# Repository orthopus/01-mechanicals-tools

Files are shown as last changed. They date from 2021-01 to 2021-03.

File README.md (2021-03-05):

# Mechanicals Tools for hand amputees




This repository contains documentation of mechanicals tools dedicated to daily life use: suitable tools to practice music, sports, cooking, etc!

For now you will find : 

- **a guitar pick holder 3D printed**
- **a tennis ball holder 3D printed** 

These tools can be used with the [ORTHOPUS' universal mechanical wrist](https://github.com/orthopus/01-wrist).

## WARNING NOTICE BEFORE STARTING

The versions of our solutions reproduced with Do It Yourself technics will not be CE marked. It can only be applied to solutions developed and sold by ORTHOPUS which follow the applicable regulations.
ORTHOPUS cannot guarantee the “quality” of solutions replicated by third parties thanks to documentation shared on github.

## GUITAR PICK HOLDER 3D PRINTED

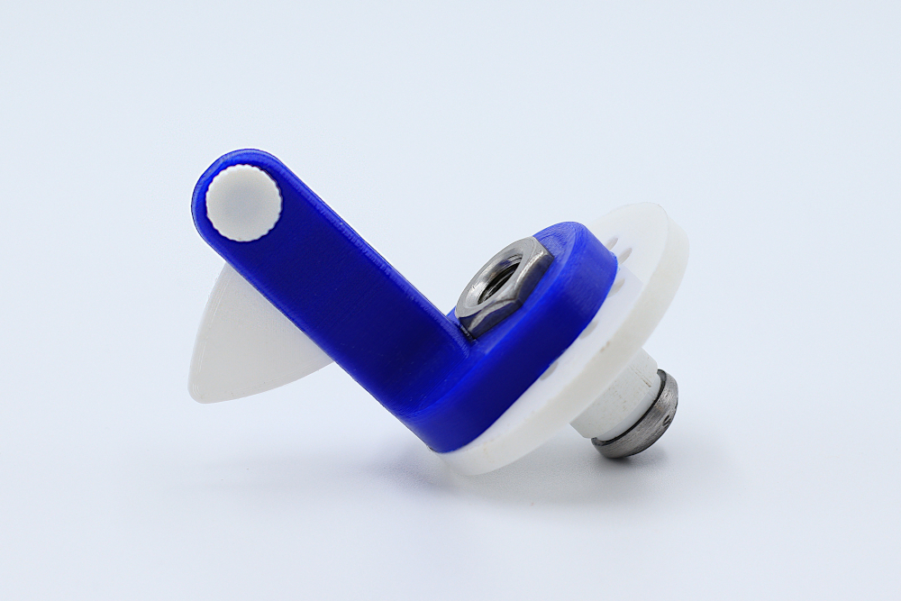
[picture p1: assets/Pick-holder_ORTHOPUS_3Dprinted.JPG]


### D.I.Y Level **⭐**

**Required components**: To make your own Pick Holder, you will need a 3D printer, a guitar pick, a Tool Holder 3D printed ([Making Manual](https://github.com/orthopus/01-wrist/blob/main/docs/tool-holder-3D-printer/ToolHolder_3D_making-manual.md)) and some basics screws (you will find a detailed list of equipment in the [Making Manual](https://github.com/orthopus/01-mechanicals-tools/blob/main/docs/PickHolder_making-manual.md))

**How to make your own**: you can make the Pick Holder for ~2€: more details in the Bill of Material shown below and available with clickable links [here](https://github.com/orthopus/01-mechanicals-tools/blob/main/src/GuitarPickHolder-3D/ILL-0307-%20Pick%20Holder%203D%20printed_BoM.pdf).

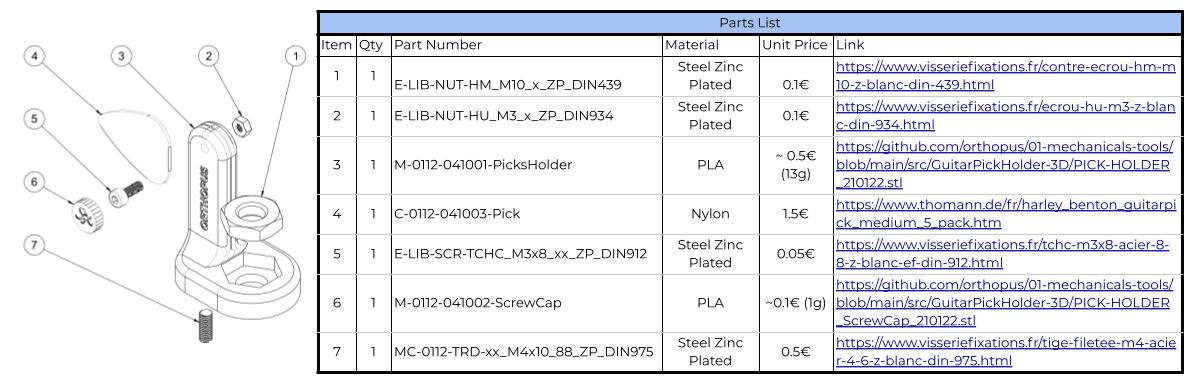
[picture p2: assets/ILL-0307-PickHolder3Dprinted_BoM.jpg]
ILL-0307-PickHolder3Dprinted_BoM


To make your own Pick Holder, follow the [Making Manual](https://github.com/orthopus/01-mechanicals-tools/blob/main/docs/PickHolder_making-manual.md).

## TENNIS BALL HOLDER 3D PRINTED

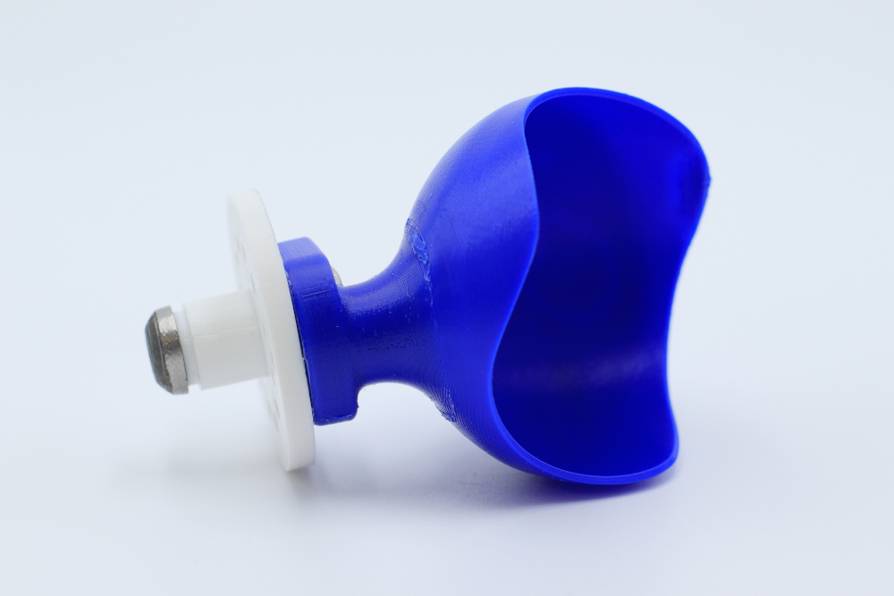
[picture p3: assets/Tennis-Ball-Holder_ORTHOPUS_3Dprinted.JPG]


### D.I.Y Level **⭐**

**Required components**: To make your own Tennis Ball Holder, you will need a 3D printer, a metal saw, a Tool Holder 3D printed ([Making Manual](https://github.com/orthopus/01-wrist/blob/main/docs/tool-holder-3D-printer/ToolHolder_3D_making-manual.md)) and some basics screws (you will find a detailed list of equipment in the [Making Manual](https://github.com/orthopus/01-mechanicals-tools/blob/main/docs/TennisBallHolder_making-manual.md)).

**How to make your own**:

You can make the Tennis Ball Holder for ~2.5€: more details in the Bill of Material shown below and available with clickable links [here](https://github.com/orthopus/01-mechanicals-tools/blob/main/src/TennisBallHolder-3D/ILL-0307-TennisBallHolder3Dprinted_BoM.pdf).

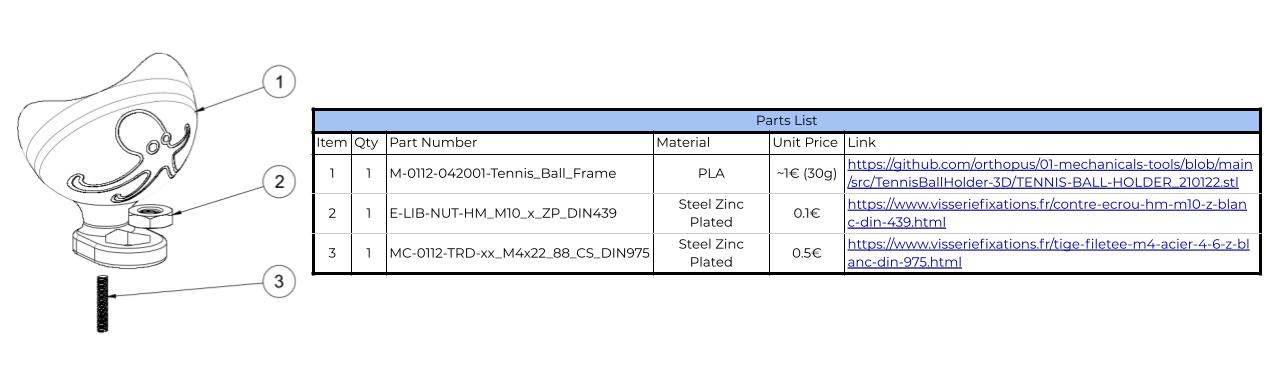
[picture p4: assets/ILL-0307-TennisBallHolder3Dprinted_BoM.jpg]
ILL-0307-TennisBallHolder3Dprinted_BoM


To make your own Tennis Ball Holder, follow the [Making Manual](https://github.com/orthopus/01-mechanicals-tools/blob/main/docs/TennisBallHolder_making-manual.md).

## CONTRIBUTION

Your contribution to the **Tennis Ball Holder v2.0** and the **Pick Holder v2.0** is welcome!

* Have you discovered a bug or you have an improvement ideas ?
  * Go to the GitHub [issues](https://github.com/orthopus/01-mechanicals-tools/issues) of the project.
* You have time, some Maker skills and you want to help us ?
  * ***If you need to make some modifications, our Fusion 360 source files are available on request, don’t hesitate to ask us!***
  * Read the [CONTRIBUTING](CONTRIBUTING‧md) file to help us to upgrade this project
  * Read the [CODEOFCONDUCT](CODEOFCONDUCT‧md) file to know community standards

## CONTACT

If you wish to contact us, you can send a message to contact@orthopus.com

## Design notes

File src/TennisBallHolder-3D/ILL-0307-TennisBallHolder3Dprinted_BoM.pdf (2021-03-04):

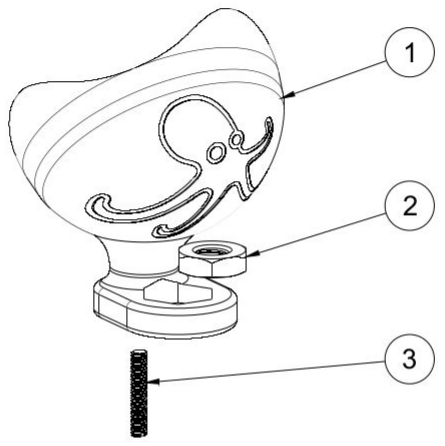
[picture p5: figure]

Parts List (please download this file for clickable links)
Item | Qty | Part Number | Material | Unit Price | Link
1 | 1 | M-0112-042001-Tennis_Ball_Frame | PLA | ~1€ (30g) | https://github.com/orthopus/01-mechanicals-tools/blob/main
/src/TennisBallHolder-3D/TENNIS-BALL-HOLDER_210122.stl (https://github.com/orthopus/01-mechanicals-tools/blob/main/src/TennisBallHolder-3D/TENNIS-BALL-HOLDER_210122.stl)
2 | 1 | E-LIB-NUT-HM_M10_x_ZP_DIN439 | Steel Zinc Plated | 0.1€ | https://www.visseriefixations.fr/contre-ecrou-hm-m10-z-blan
3 | 1 | MC-0112-TRD-xx_M4x22_88_CS_DIN975 | Steel Zinc Plated | 0.5€ | https://www.visseriefixations.fr/tige-filetee-m4-acier-4-6-z-bl

c-din-439.html (https://www.visseriefixations.fr/contre-ecrou-hm-m10-z-blanc-din-439.html)

anc-din-975.html (https://github.com/orthopus/01-mechanicals-tools/blob/main/src/GuitarPickHolder-3D/PICK-HOLDER_210122.stl)

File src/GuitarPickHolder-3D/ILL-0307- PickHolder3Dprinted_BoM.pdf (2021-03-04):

Parts List (please download this file for clickable links)
Item | Qty | Part Number | Material | Unit Price | Link
1 | 1 | E-LIB-NUT-HM_M10_x_ZP_DIN439 | Steel Zinc Plated | 0.1€ | https://www.visseriefixations.fr/contre-ecrou-hm-m

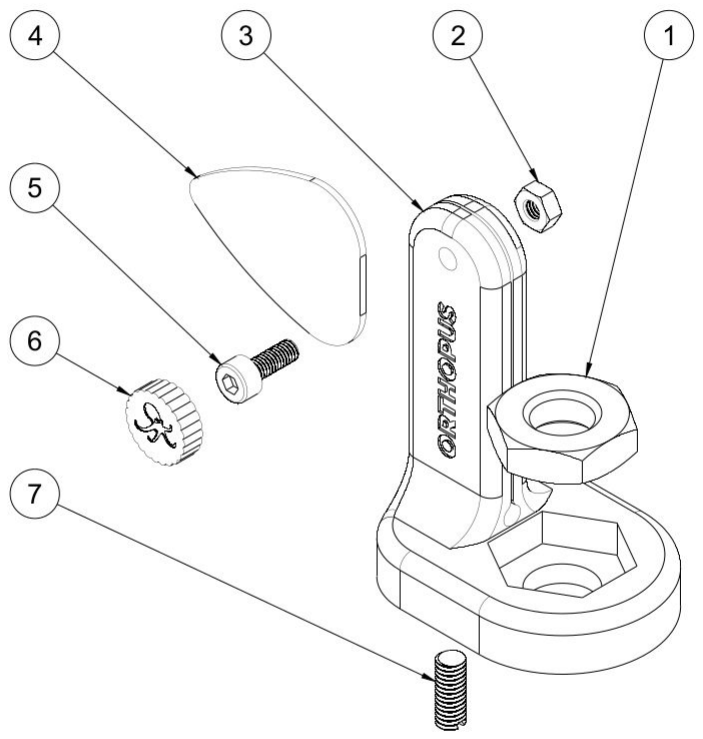
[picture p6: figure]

2 | 1 | E-LIB-NUT-HU_M3_x_ZP_DIN934 | Steel Zinc Plated | 0.1€ | https://www.visseriefixations.fr/ecrou-hu-m3-z-blan
3 | 1 | M-0112-041001-PicksHolder | PLA | ~ 0.5€ (13g) | https://github.com/orthopus/01-mechanicals-tools/blob/main/src/GuitarPickHolder-3D/PICK-HOLDER
4 | 1 | C-0112-041003-Pick | Nylon | 1.5€ | https://www.thomann.de/fr/harley_benton_guitarpi
5 | 1 | E-LIB-SCR-TCHC_M3x8_xx_ZP_DIN912 | Steel Zinc Plated | 0.05€ | https://www.visseriefixations.fr/tchc-m3x8-acier-8-

10-z-blanc-din-439.html (https://www.visseriefixations.fr/contre-ecrou-hm-m10-z-blanc-din-439.html)

c-din-934.html (https://www.visseriefixations.fr/ecrou-hu-m3-z-blanc-din-934.html)

_210122.stl (https://github.com/orthopus/01-mechanicals-tools/blob/main/src/GuitarPickHolder-3D/PICK-HOLDER_210122.stl)

ck_medium_5_pack.htm (https://www.thomann.de/fr/harley_benton_guitarpick_medium_5_pack.htm)

8-z-blanc-ef-din-912.html (https://www.visseriefixations.fr/tchc-m3x8-acier-8-8-z-blanc-ef-din-912.html)
6 | 1 | M-0112-041002-ScrewCap | PLA | ~0.1€ (1g) | https://github.com/orthopus/01-mechanicals-tools/blob/main/src/GuitarPickHolder-3D/PICK-HOLDER
7 | 1 | MC-0112-TRD-xx_M4x10_88_ZP_DIN975 | Steel Zinc Plated | 0.5€ | https://www.visseriefixations.fr/tige-filetee-m4-acie

_ScrewCap_210122.stl (https://github.com/orthopus/01-mechanicals-tools/blob/main/src/GuitarPickHolder-3D/PICK-HOLDER_ScrewCap_210122.stl)

r-4-6-z-blanc-din-975.html (https://www.visseriefixations.fr/tige-filetee-m4-acier-4-6-z-blanc-din-975.html)

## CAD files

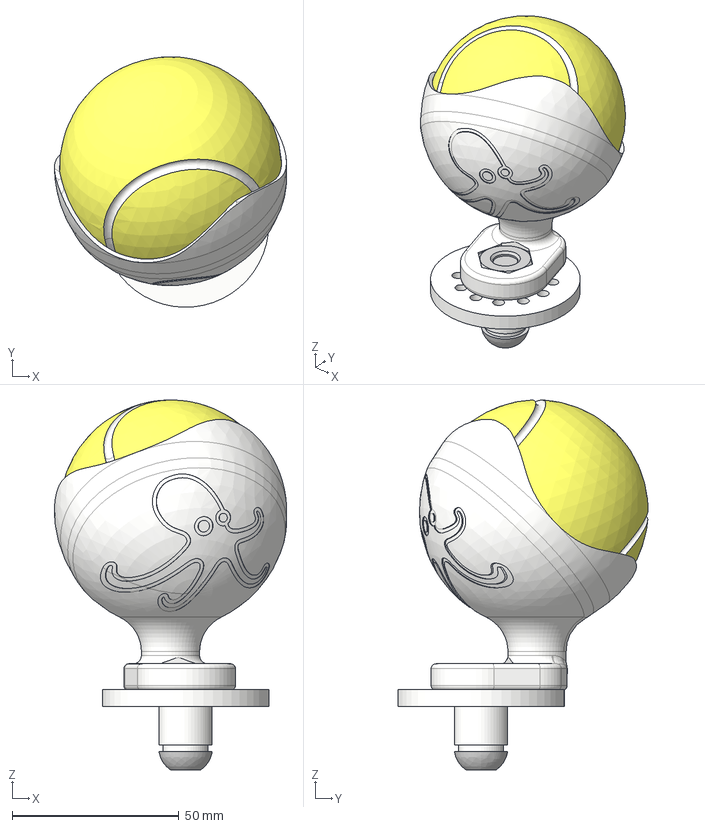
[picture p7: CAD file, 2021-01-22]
src/TennisBallHolder-3D/TENNIS-BALL-HOLDER_210122.step
69.7 x 75.2 x 111.1 mm
M-0109-03_1481-AttachmentPlate_3DP
MC-0109_1482-TBHC_M10X25_00_CS_ISO7380
M-0112-042001-Tennis_Ball_Frame
C-0112-042002-Tennis_Ball
MC-0112-TRD-xx_M4x22_88_CS_DIN975

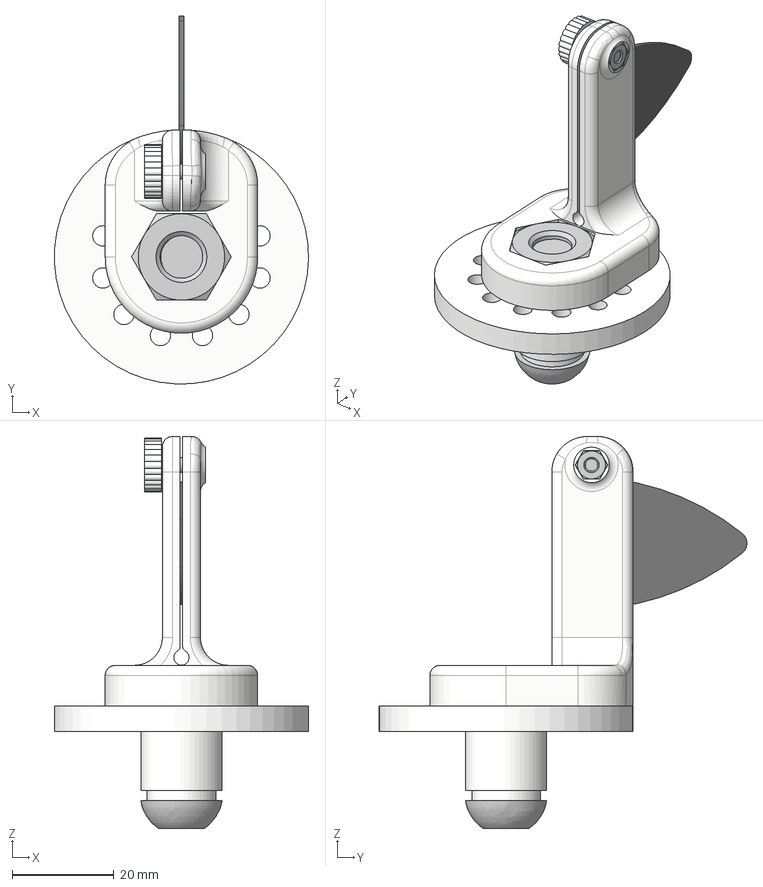
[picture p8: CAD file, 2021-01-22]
src/GuitarPickHolder-3D/PICK-HOLDER_210122.step
50.0 x 72.3 x 77.1 mm
M-0112-041001-PicksHolder
M-0112-041002-ScrewCap
C-0112-041003-Pick
MC-0112-TRD-xx_M4x10_88_CS_DIN975
M-0109-03_1481-AttachmentPlate_3DP
MC-0109_1482-TBHC_M10X25_00_CS_ISO7380

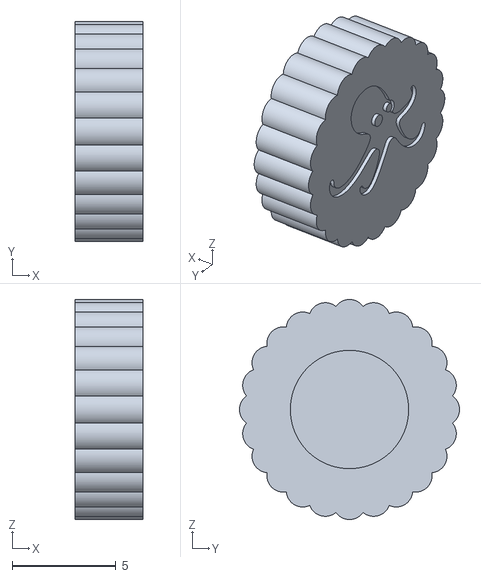
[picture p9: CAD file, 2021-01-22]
src/GuitarPickHolder-3D/PICK-HOLDER_ScrewCap_210122.stl
3.30 x 10.6 x 10.6

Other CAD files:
src/GuitarPickHolder-3D/PICK-HOLDER_210122.stl
src/TennisBallHolder-3D/TENNIS-BALL-HOLDER_210122.stl

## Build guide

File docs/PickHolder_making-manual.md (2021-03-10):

# Pick Holder 3D : Making Manual

In this manual, you will find all the resources to design the ORTHOPUS 3D printed Pick Holder.

Pick-holder_ORTHOPUS_3Dprinted

### **List of Equipment**

**To design the Pick Holder you will need :**

- PLA type filament
- A Tool Holder 3D printed ([Making Manual](https://github.com/orthopus/01-wrist/blob/main/docs/tool-holder-3D-printer/ToolHolder_3D_making-manual.md))
- A threaded rod M4, zinc plated, DIN 975
- A screw (CHC M3x8, zinc plated, DIN 912)
- A bolt (Hu M3, zinc plated, DIN 934)

More details in the Bill of Material shown below and available with clickable links [here](https://github.com/orthopus/01-mechanicals-tools/blob/main/src/GuitarPickHolder-3D/ILL-0307-%20PickHolder3Dprinted_BoM.pdf).

ILL-0307-PickHolder3Dprinted_BoM

**Tools :**

- A 3D Printer

- Cyanoacrylate glue (super glue)

### **The 3D printed body**

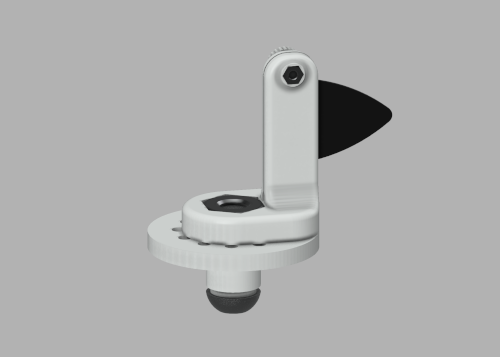
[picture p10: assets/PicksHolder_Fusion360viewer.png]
PicksHolder_Fusion360viewer (https://a360.co/3dsERMs)


🧐 *Tip : open the image in a new tab to view the Pick Holder in Fusion 360 viewer*

The 3D printed body of the **Pick Holder** will firmly hold guitar picks. It will allow you through a tightening system to adjust the position and to adapt to the thickness of the guitar pick. This body needs to be connected to the **[Tool Holder 3D printed](https://github.com/orthopus/01-wrist).**

The 2 .STL file are available in [the SRC repository](https://github.com/orthopus/01-mechanicals-tools/tree/main/src/GuitarPickHolder-3D)

We used the Ultimaker Cura slicer and an Ultimaker Extended 2+ 3D printer. Following parameter were used:

- Layer height: 0.15 mm

- Infill density: 50%

- Print speed: 50 mm/s

- Fan speed: 100%

- Build plate adhesion type: Brim

### **Machining Operation**

To avoid the pick holder to get loose from the tool holder 3D printed, a modified threaded rod needs to be made. With a metal saw, saw a M4 threaded rod or a M4 screw to get a 10 mm threaded part. To be able to screw this threaded part inside the Pick Holder, it is necessary to make a slot at one end of it. Using the saw, make a ~1 mm deep slot to be able to use a flat screwdriver to screw the threaded part inside the Tennis Ball Holder.

You should get the following part:

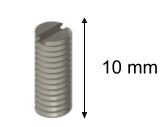
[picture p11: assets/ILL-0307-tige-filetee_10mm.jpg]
ILL-0307-tige-filetee_10mm


### **Assembly**

- **Assembly of the pick holder 3D printed:**

1. First, insert the 10 mm long threaded rod into the 3D printed body with a flat screwdriver. 
2. Glue the head of the screw in the screw cap. 
3. Place the M3 bolt in its housing. Then insert inside the screw with the glued cap.
4. You can now insert a guitar pick in the slot. You need to adjust the position of the screw to let the pick in the slot and then to hold it firmly.

- **Assembly of the pick holder 3D printed onto the Tool Holder 3d printed:**

1. Place the M10 bolt in its housing and the 3D printed body over the Tool Holder 3D Printed (a Tool Holder 3D printed [Making Manual](https://github.com/orthopus/01-wrist/blob/main/docs/tool-holder-3D-printer/ToolHolder_3D_making-manual.md)). Be careful to place the 10 mm long threaded rod into the specific hole of the Tool Holder 3D Printed.

2. Screw the M10 modified screw in the M10 bolt.

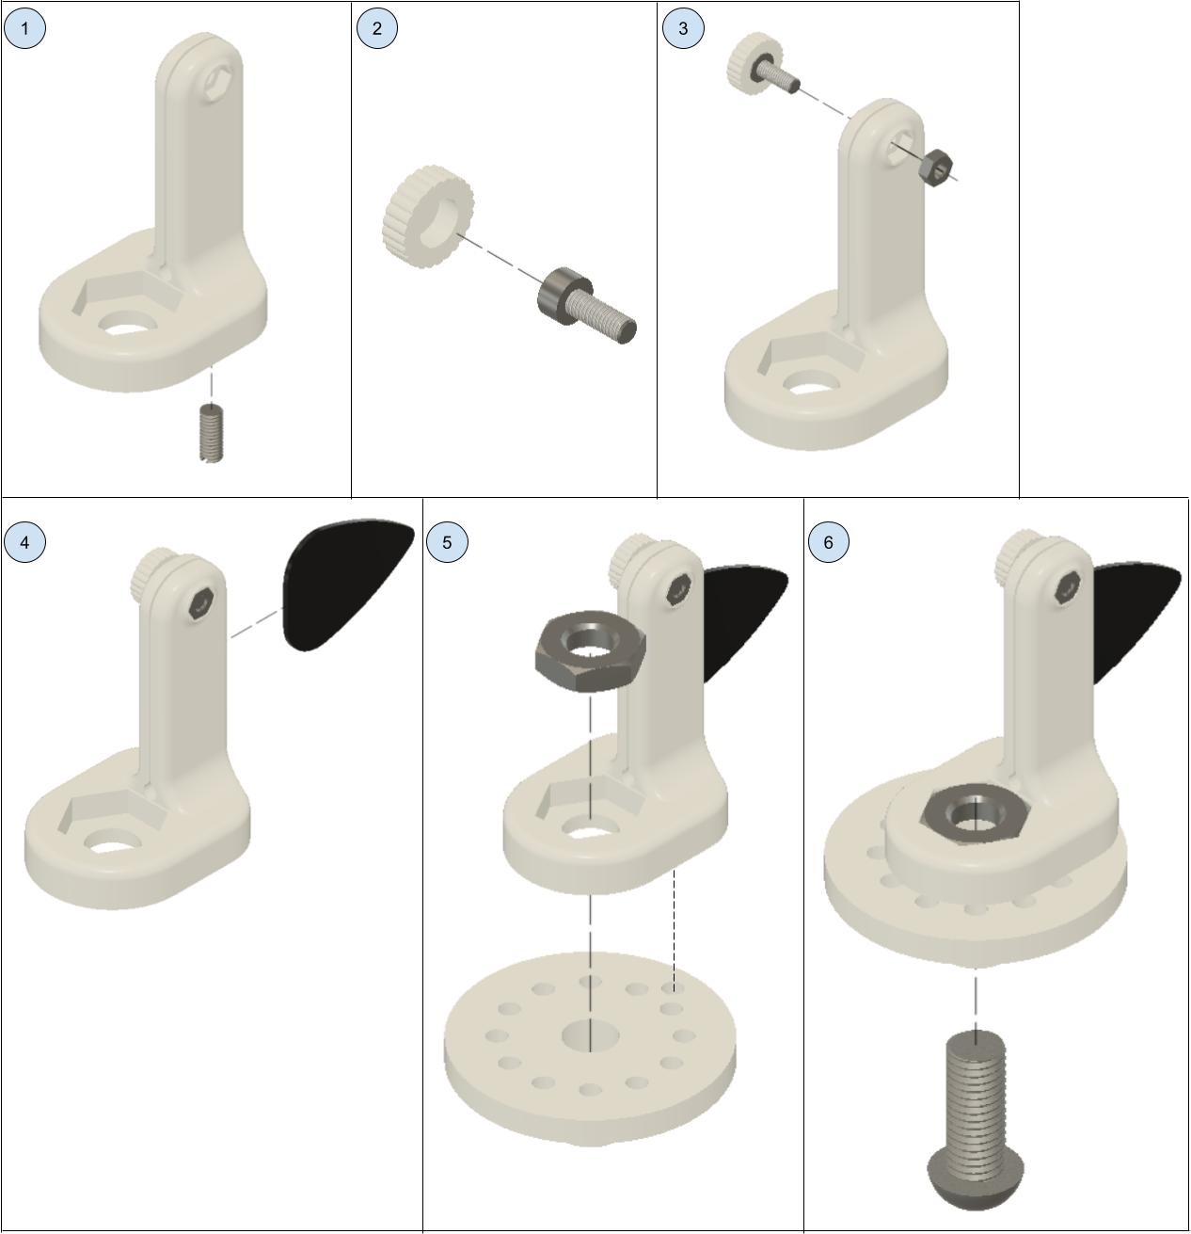
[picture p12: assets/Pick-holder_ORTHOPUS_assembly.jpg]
Pick-holder_ORTHOPUS_assembly


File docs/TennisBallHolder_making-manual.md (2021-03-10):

# Tennis Ball Holder : Making Manual

Tennis-Ball-Holder_ORTHOPUS_3Dprinted

In this manual, you will find all the resources to design the ORTHOPUS' 3D printed Tennis Ball Holder.

### **List of Equipment**

**To design the Tennis Ball Holder you will need :**

- PLA type filament
- A Tool Holder 3D printed [Making Manual](https://github.com/orthopus/01-wrist/blob/main/docs/tool-holder-3D-printer/ToolHolder_3D_making-manual.md)
- A threaded rod M4, zinc plated, DIN 975
- a Tool Holder 3D printed

More details in the Bill of Material shown below and available with clickable links [here](https://github.com/orthopus/01-mechanicals-tools/blob/main/src/TennisBallHolder-3D/ILL-0307-TennisBallHolder3Dprinted_BoM.pdf).

ILL-0307-TennisBallHolder3Dprinted_BoM

**Tools :** 

- A metal saw
- A 3D Printer

### **The 3D printed body** 

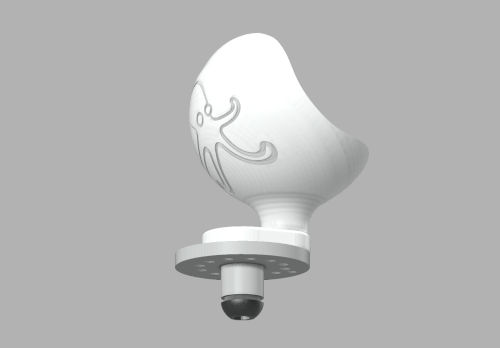
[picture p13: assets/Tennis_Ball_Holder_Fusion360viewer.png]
Tennis_Ball_Holder_Fusion360viewer (https://a360.co/30sFVIv)


🧐 *Tip : open the image in a new tab to view the Tennis Ball Holder in Fusion 360 viewer*

The **Tennis Ball Holder** will house the tennis ball. It will allow you to throw the tennis ball and to serve as a pro! The 3D printed body of the Tennis ball Holder needs to be connected to the **[Tool Holder 3D printed](https://github.com/orthopus/01-wrist).** Thus, to make a Tennis Ball Holder compatible with the Universal Wrist you need to assemble the 3D printed body with a **[Tool Holder 3D printed](https://github.com/orthopus/01-wrist).**

The .STL file are available [here](https://github.com/orthopus/01-mechanicals-tools/tree/main/src/TennisBallHolder-3D)

We used the Ultimaker Cura slicer and an Ultimaker Extended 2+ 3D printer.

**Following parameter were used:**

- Layer height: 0.15 mm
- Infill density: 50%
- Print speed: 50 mm/s
- Fan speed: 100%
- Build plate adhesion type: Brim

### **Machining Operation**

To avoid the tennis ball holder to get loose from the tool holder 3D printed, a modified threaded rod needs to be made. With a metal saw, saw a M4 threaded rod or a M4 screw to get a 22 mm threaded part. To be able to screw this threaded part inside the Tennis Ball Holder, it is necessary to make a slot at one end of it. Using the saw, make a ~1 mm deep slot to be able to use a flat screwdriver to screw the threaded part inside the Tennis Ball Holder.

You should get the following part:

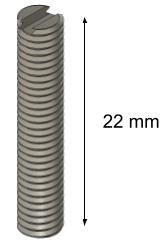
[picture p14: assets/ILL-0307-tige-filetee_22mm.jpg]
ILL-0307-tige-filetee_22mm


### **Assembly**

**Assembly of the Tennis ball holder 3D printed:**

1. First, insert the 22 mm long threaded rod into the 3D printed body with a flat screwdriver.

**Assembly of the Tennis ball holder 3D printed onto the Tool Holder 3D printed**:

1. Place the M10 bolt in its housing and the 3D printed body over the Tool Holder 3D Printed (a Tool Holder 3D printed [Making Manual](https://github.com/orthopus/01-wrist/blob/main/docs/tool-holder-3D-printer/ToolHolder_3D_making-manual.md)). Be careful to place the 22 mm long threaded rod into the specific hole of the Tool Holder 3D Printed.

2. Screw the M10 modified screw in the M10 bolt.

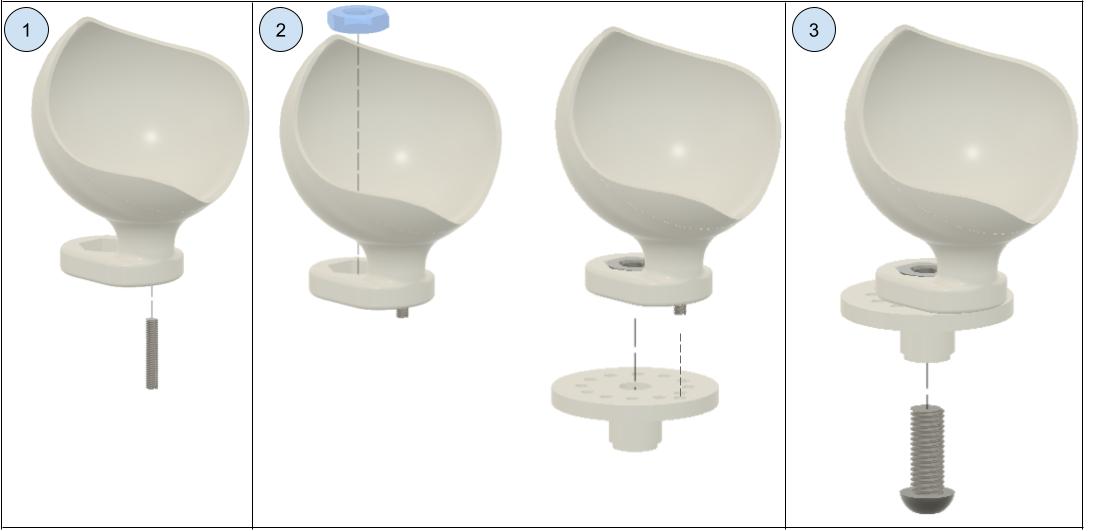
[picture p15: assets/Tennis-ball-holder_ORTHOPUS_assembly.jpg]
Tennis-ball-holder_ORTHOPUS_assembly


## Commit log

2021-01-22 base files
    [PICK-HOLDER_210122.step, PICK-HOLDER_210122.stl, PICK-HOLDER_ScrewCap_210122.stl, TENNIS-BALL-HOLDER_210122.step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]
2021-02-17 Update README.md
    TEST de Tibo, correction des prix et de qqs fautes de frappe
2021-02-17 Update README.md
    Correction URL vers tennis ball holder.md + ajout tool holder dans required devices
2021-02-22 Add files via upload
    ajout BoM en CSV
    [BOM-0307-Pick Holder.csv]
2021-03-04 Delete BOM-0307-Pick Holder.csv
    deleted because not useful anymore
    [BOM-0307-Pick Holder.csv]
